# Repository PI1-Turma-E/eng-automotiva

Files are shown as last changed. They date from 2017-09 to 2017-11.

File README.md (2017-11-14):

# Eng-automotiva

# AR2

A AR2 it the robotic arm chosen for use on ultrasound long-distance exam because of it's open source origin.

The arm is converted from the original STEP files to work on CATIA. There is still need to put on bearings and screws on the assembly and to modify or create some stuff to make it work on the final project.

## 6 axis stepper motor robot

This project includes:

- CAD on catia format for working
- Kinematic model

Should be noted that i deleted everything that isn't related to the CAD files.

All geared stepper motors and drivers are available from  [www.omc-stepperonline.com](https://www.omc-stepperonline.com/?tracking=59c1139e8987b) and all other misc. hardware are off-the-shelf items available from multiple sources (see the bill of materials file).

## Information

quick note: **Read the TODO**

really important: **Use the CATIA v5 r19 version** 

Everything here was laid down to us by the guy below, so please pay credit to him.

original git: https://github.com/Chris-Annin/AR2 

Some of the needed parts we will find on [McMaster-carr](https://www.mcmaster.com/)

On the end, we will need to make all the files to print again, as we change the model to fit our needs. If not, we could simply use the original git files to print

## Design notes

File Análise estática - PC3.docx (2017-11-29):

Análise estática

A aplicada ao modelo está presente na figura 1. É possível observar no índice da foto a qualidade dos elementos criados. Em maioria os elementos estão bons para análise estática.

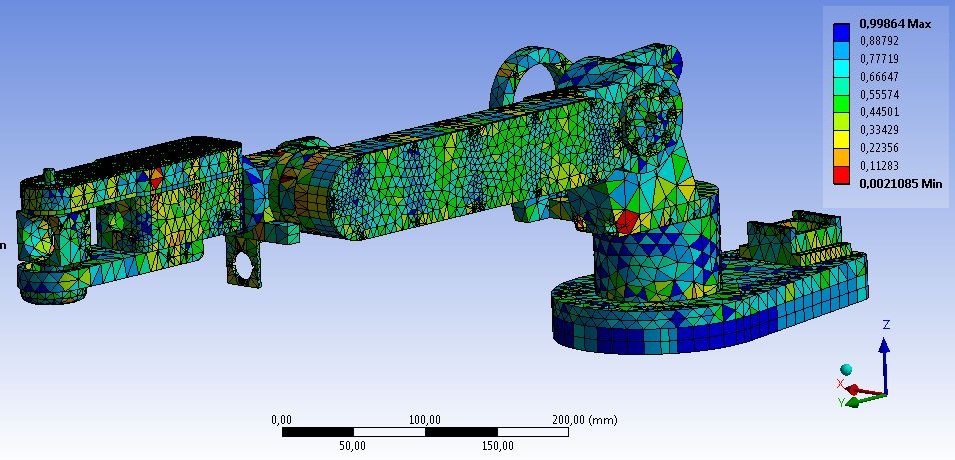
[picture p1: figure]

Figura 1 - Qualidade dos elementos da malha.

Os tipos de elementos utilizados pelo software estão apresentados na figura 2. Os próprios software que gerou os elementos que em maioria são do tipo SOLID187 e SOLID 186.

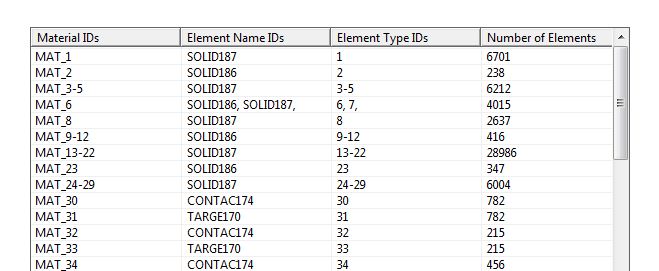
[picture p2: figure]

Figura 2 - Tipos de elementos utilizados na simulação.

As condições de contorno aplicadas foram baseadas no funcionamento estático do braço. O objetivo foi determinar se o material empregado no corpo do braço suportaria o carregamento dos motores e do levantamento do ultrassom. Os locais de aplicação das forças estão representados na figura 3.

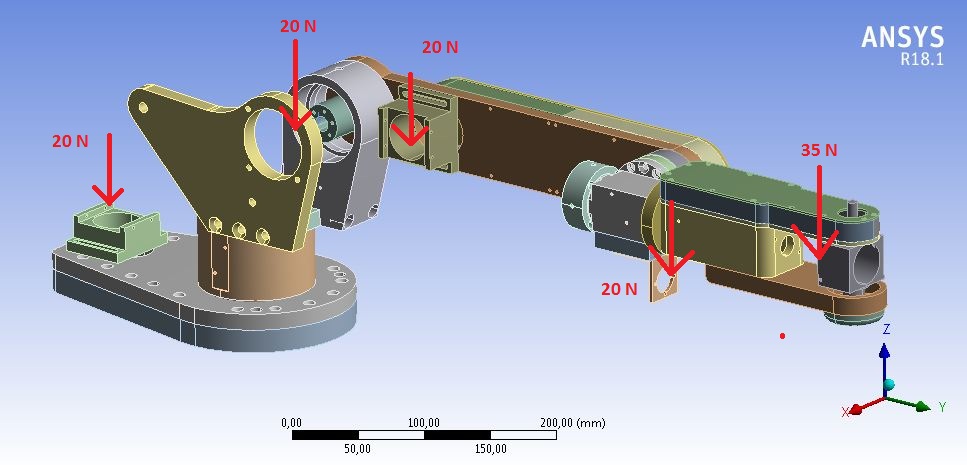
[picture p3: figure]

Figura 3 - Condições de contorno.

Baseado no critério de von Mises, a estrutura teve uma solicitação máxima de aproximadamente 13 mPa. Nessas condições o material empregado suporta as condições estáticas. A figura 4 apresenta esses resultados.

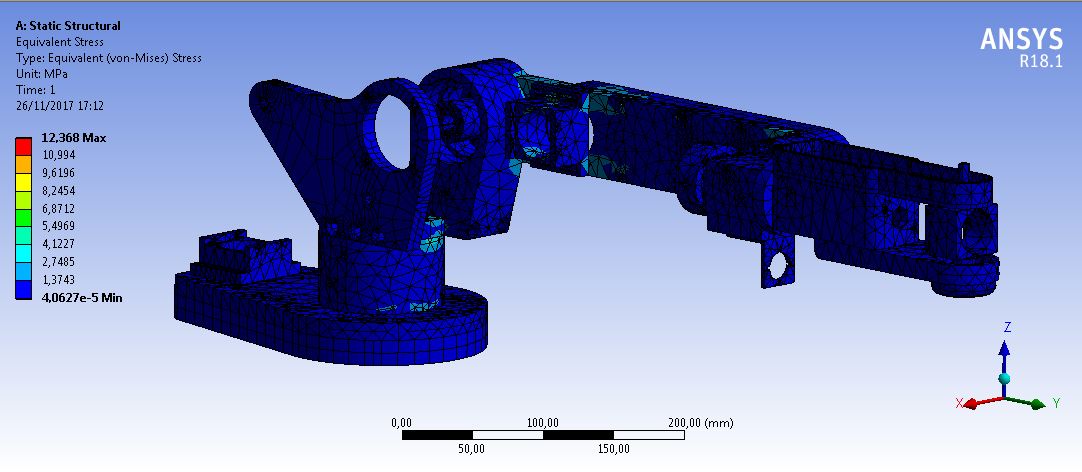
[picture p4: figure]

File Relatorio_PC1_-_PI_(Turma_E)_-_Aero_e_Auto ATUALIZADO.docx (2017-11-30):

Análise e detalhamento de requisitos para o Projeto de Implementação de sistema de telemedicina para exames de ultrassom à distância (Eng. Automotiva/Aeroespacial)

Projeto Integrador 1 – Turma E
Profª: Mariana Costa Bernardes Dias

Gerente de área: Marcos Paulo Miranda Costa

Introdução

Como parte do escopo do Projeto de Implementação de sistema de telemedicina para exames de ultrassom à distância, foi delegada para os alunos das Engenharias Automotiva e Aeroespacial a construção de um braço mecânico capaz de movimentar o transdutor responsável pelo exame de ultrassom. A peça seria uma das partes essenciais do projeto, que tem o objetivo de viabilizar para comunidades carentes e regiões distantes dos grandes centros urbanos a realização de exames de ultrassom e o acesso ao atendimento médico de qualidade.
Para atender às necessidades de projeto, foi definida uma série de pré-requisitos iniciais, dentre os quais estão a capacidade da peça em se movimentar com eficiência (translação e rotação), a leveza dos materiais e a transportabilidade do braço em caso de transferência de equipamentos, bem como a confiabilidade e segurança das peças para a utilização em ambiente hospitalar (médico). Todos os requisitos estabelecidos são devidamente detalhados ao longo deste trabalho. Uma vez que o objetivo do projeto está em realizar exames à distância, também fora decidido que o braço mecânico teria de ser controlado por meio de mecanismos eletrônicos, com base na manipulação de um joystick por um médico especializado em uma unidade de controle pré-definida. O controle do equipamento seria então efetuado via internet, sem que fosse necessária a presença do médico nos locais de exame, estes muitas vezes de difícil acesso.
O projeto foi efetuado numa colaboração entre os alunos das Engenharias Automotiva, Aeroespacial, Eletrônica, Energia e de Software, durante a disciplina de Projeto Integrador 1 da Universidade de Brasília (UnB) – Campus Gama. Cada área tornou-se responsável por uma função no projeto, com o objetivo de entregar ao final da disciplina um protótipo funcional da ideia inicialmente proposta pelo professor.

Objetivo

O objetivo do presente trabalho consiste na construção de um braço mecânico capaz de movimentar o transdutor responsável pela realização de exames de ultrassom. Como exigências para o projeto estão a liberdade de movimentação do equipamento (translação e rotação), a leveza dos materiais constituintes e transportabilidade da peça como um todo, assim como a segurança e a confiabilidade da mesma. O braço mecânico constitui uma das partes essenciais do Projeto de Implementação de sistema de telemedicina para exames de ultrassom à distância.


Metodologia

Para que fosse possível a implementação do projeto, o grupo constituído pelos alunos das Engenharias Automotiva e Aeroespacial foi dividido em dois subgrupos de pesquisa e desenvolvimento. O primeiro teve como objetivo a criação de um protótipo em CAD (Catia e/ou similares) reunindo características essenciais do projeto, a exemplo de suas dimensões, formato, materiais, análise estrutural, encaixe de peças, etc no intuito de trazer uma perspectiva concreta do que seria construído em um aparelho real. Para alcançar tal objetivo, o grupo de trabalho teve ainda que pesquisar e analisar iniciativas semelhantes à proposta estabelecida para o braço mecânico, com a intenção de conhecer melhor os equipamentos já desenvolvidos na área médica para tal fim. O segundo subgrupo criado, por sua vez, teve a função de análise e escolha dos materiais que irão compor o braço mecânico como um todo. Questões como leveza, transportabilidade, viabilidade econômica e usinabilidade dos materiais foram extensamente analisadas por este grupo para enfim determinar do que seria construído o braço mecânico. Ambos os grupos tiveram que fundamentar sua pesquisa em normas e características que fornecessem segurança e confiabilidade, tanto para a execução do projeto quanto para o funcionamento do equipamento.

Projeto do braço mecânico em CAD

Inicialmente, para o projeto do braço mecânico, foi necessário definir quais funções o equipamento teria de executar. Nesse contexto, foram consultados artigos e referências na área médica relativa a exames de ultrassom, para se ter uma noção do que seria necessário implementar no projeto da peça. Após o período de pesquisa, e segundo[1][3][4][5], a construção do braço mecânico teve que levar em consideração fatores como mobilidade, capacidade de carregar um transdutor de 400g e ter movimentação eficiente em translação e rotação, alto grau de precisão, leveza e transportabilidade de materiais, bem como a segurança em um ambiente hospitalar. Para os fins do projeto da disciplina, o equipamento teria ainda que atender a requisitos de viabilidade econômica.
Dentre as iniciativas encontradas no mercado, uma chamou a atenção em específico por conter todas as características exigidas para o projeto. Trata-se de um braço mecânico desenvolvido por Chris Annin [6]. O braço mecânico de Chris Annin foi escolhido graças ao seu alto grau de precisão e segurança durante o contato com o paciente. O grupo de trabalho decidiu tomar o projeto como base para a confecção de um braço semelhante, mas com a capacidade de ser controlado à distância via internet por um joystick manipulado por um médico especializado em uma unidade de controle pré-definida.









O braço mecânico teria o seguinte formato:


Figura 1: Desenho Braço mecânico para uso na área biomédica. Fonte: BATALHA, Wagner Clemente Coelho, Projeto da disciplina Projeto Integrador 1 da Faculdade do Gama, FGA-UNB. Brasília, DF, Brasil, 2017.

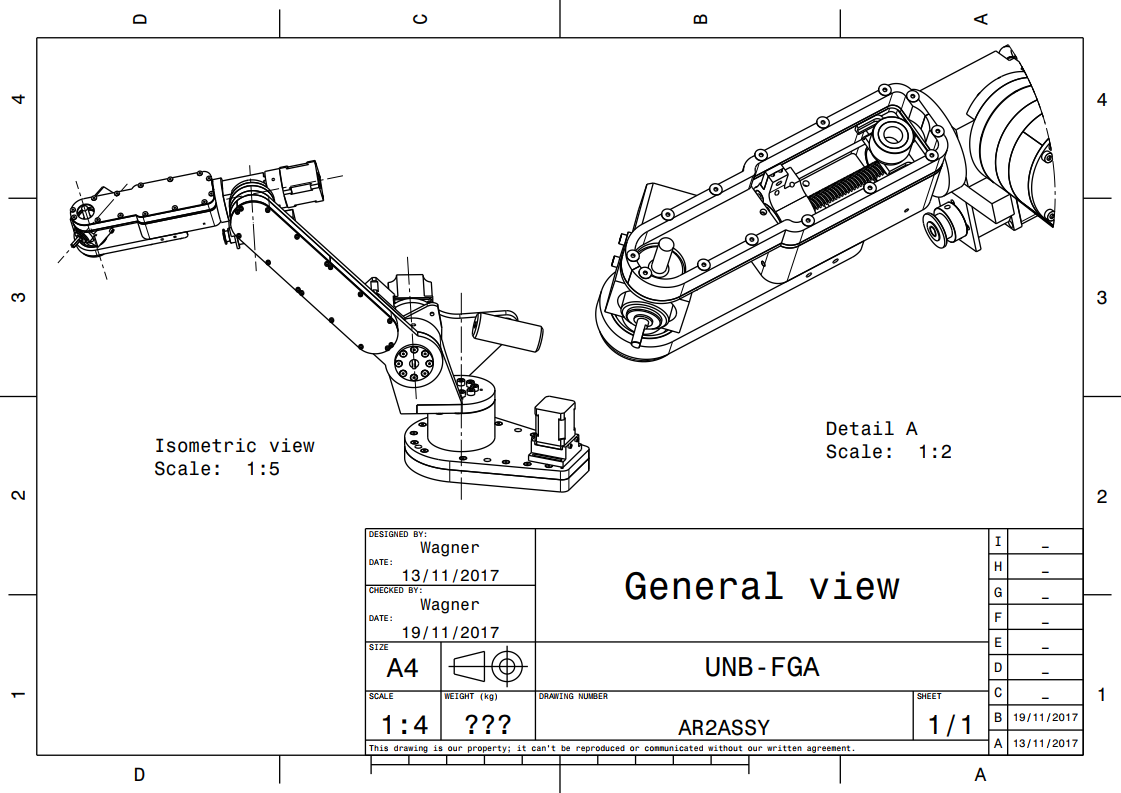
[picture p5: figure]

O formato e a constituição do equipamento como é descrito na Figura 1 se deve aos requisitos citados anteriormente. Este modelo contará com 6 motores de passo em suas articulações e em sua base, o que fornece alto grau de precisão e facilidade em seus controles a distância. Os materiais escolhidos para o projeto foram escolhidos com foco em alcançar o menor peso possível ao final do projeto para maior facilidade de locomoção de suas peças e transporte do braço. Em tópicos posteriores será explicado melhor sobre os materiais. O transdutor de 400g conseguirá ser carregado com firmeza peço braço graças a firmeza dos materiais. No trabalho em questão, este será o modelo de braço mecânico a ser construído, com as dimensões definidas de acordo com as necessidades do projeto na parte de Software e Eletrônica. Em conjunto com o grupo de alunos das Engenharias Eletrônica e de Software, o braço será aprimorado com o controle automático à distância, e a inserção desta tecnologia está por conta da análise e pesquisa prévia destes integrantes de projeto.
A modelagem em CAD do braço mecânico foi efetuado no software Catia V5R19, assim como a descrição das medidas e o desenho técnico das peças constituintes. Para a construção do protótipo, será também necessário o uso de uma impressora 3D que, pela facilidade de acesso e viabilidade econômica de materiais, irá proporcionar ao grupo de trabalho a possibilidade de verificar se o braço construído funcionará de maneira satisfatória.

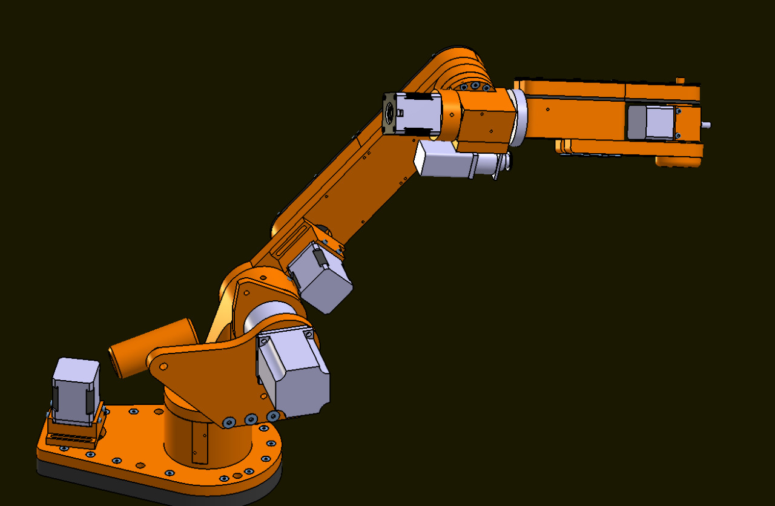
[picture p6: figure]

Figura 2: Desenho 3D do braço mecânico para uso na área biomédica. BATALHA, Wagner Clemente Coelho. Projeto da disciplina Projeto Integrador 1 da Faculdade do Gama, FGA-UNB. Brasília, DF, Brasil,2017.

Pesquisa, análise e escolha de materiais

O projeto apresenta um requisito fundamental para a construção de um braço mecânico, os materiais. Para que se tenha uma otimização melhor do projeto final, é necessário um conhecimento dos materiais a serem utilizados para que eles sejam leves, compactos e perfeitamente transportáveis. O objetivo desta parte do projeto, é definir ou se aproximar ao máximo dos materiais a serem utilizados na construção do braço mecânico. Nesse contexto, após diversos materiais estudados, chegou-se à conclusão de que materiais de impressora 3D poderiam ser utilizados em várias partes do braço mecânico. Por ser um material barato, diminuiria imensamente os custos do projeto se comparado a outros materiais.
Os materiais observados para o projeto são o ABS (acrilonitrilabutadieno estireno) [2], PETG (Politereftalato de etileno glicol) [2] e o alumínio.
O primeiro, ABS, é um material termoplástico derivado do petróleo amplamente utilizado na indústria, um dos principais e mais antigos materiais que vem sido utilizados na impressão 3D. É rígido, bom, ótima resistência a impactos, possui uma leve flexibilidade quando comparada a outros materiais, permitido uma pequena deformação ou flexão da peça,dependendo da sua geometria, o que é bom para peças que necessitem de encaixes em sua montagem. Além de muito resistente a impactos, também é resistente a temperaturas altas.
O segundo, PETG, é um material termoplástico derivado do petróleo, porém reciclável assim como o PET, utilizados na indústria há vários anos para diversas finalidades, mas, recentemente, sendo usando na impressão 3D. Apresenta um aspecto transparente e brilhoso. Produz peças tão resistentes a impactos quanto ao ABS, mas com flexilidade e resistência ligeiramente superior a este. Resiste às altas temperaturas, mas não tanto como o ABS. O que o torna ideal para peças que precisem de transparência ou encaixes com maior flexibilidade, mantendo a alta resistência.

Tabela 1. Comparação entre PETG e ABS

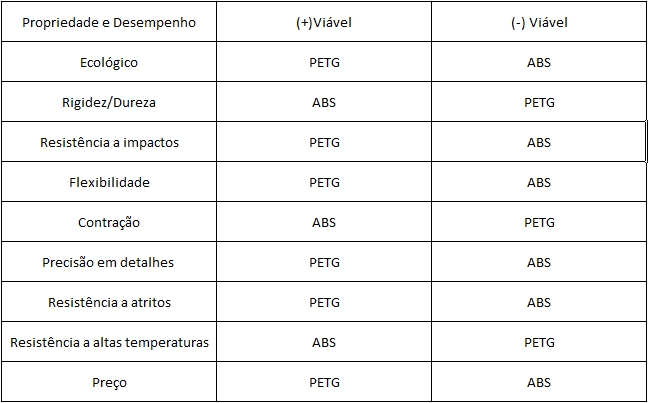
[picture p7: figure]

Analisando a tabela 1 é perceptível que o material termoplástico PETG é mais qualificado devido ao maior número de propriedades mais viáveis. Mas caso os critérios observados favoreçam o material ABS, nada o impede de ser selecionado para o projeto final do braço mecânico.

O terceiro material para analise, o alumínio, é um dos materiais mais utilizados no mundo para fins semelhantes. São inúmeras razões para escolha desse material, podendo ser citadas sua elevada resistência mecânica, sua aparência elegante para hospitais e centro de saúdes, seu valor baixo em comparação a outros metais no mercado, sua leveza e maleabilidade, longa durabilidade, segurança (sendo um material à prova de fogo), durabilidade, alta resistência térmica e baixa necessidade de manutenção. Todas essas razões fazem do alumínio a principal e a mais provável escolha para a construção do braço mecânico.

Para maior organização dos materiais necessários para a construção do braço mecânico AR2, foi montado o Bill of Material (BOM) do projeto, contendo quantidade necessária e a fonte de cada peça.

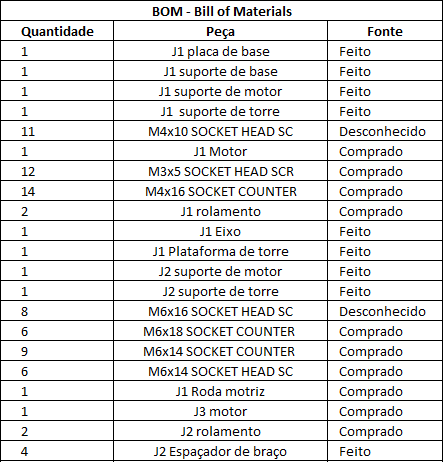
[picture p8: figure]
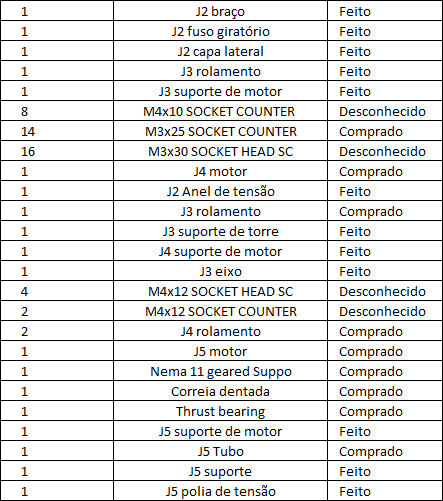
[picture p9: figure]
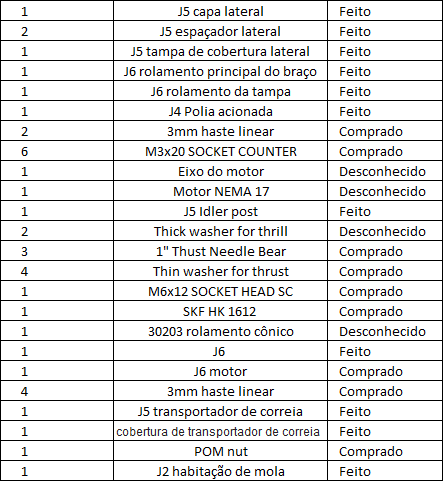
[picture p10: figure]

Figura 3: Bill of Material do braço mecânico. BATALHA, Wagner Clemente Coelho. Projeto da disciplina Projeto Integrador 1 da Faculdade do Gama, FGA-UNB. Brasília, DF, Brasil,2017.

Conclusão

A construção de um braço mecânico para atender ao Projeto de Implementação de sistema de telemedicina para exames de ultrassom à distância foi dividida em dois subgrupos de trabalho. O primeiro teve que se comprometer na realização de um protótipo em CAD reunindo as informações essenciais do projeto. Nesse caso, a aplicação dos conceitos desenvolvidos em Desenho Mecânico Assistido por Computador, bem como o conhecimento em Materiais de Construção para Engenharia foram fundamentais para que fosse possível implementar o protótipo. O segundo subgrupo, por sua vez, ficou por conta da análise, pesquisa e escolha dos materiais que iriam constituir o braço mecânico como um todo. Ambas as divisões de trabalho possibilitaram aos integrantes de projeto a aplicação de seus conceitos teóricos desenvolvidos em sala e a capacidade de desenvolver, na prática, um protótipo inovador e funcional para uma aplicação na área biomédica. O projeto ainda foi de fundamental importância para a compreensão do propósito da Engenharia em melhorar a qualidade de vida de muitas pessoas.

Referências bibliográficas

[1] NUNES, LUIS F. DE OLIVEIRA MELLO,Projeto e fabricação de um braço mecânico para ultrassom médico,Projeto de graduação, UFRJ/ESCOLA POLITÉCNICA, Rio de Janeiro, RJ, Brasil, 2015.

[2] Conheça os diferentes tipos de materiais para impressão 3D FDM. 1 Dez. 2015. IMPRESSAO3DFACIL. Disponível em: <http://www.impressao3dfacil.com.br/conheca-os-diferentes-tipos-de-materiais-para-impressao-3d-fdm/>. Acesso em: 16 Set. 2017.

[3]Richard S. Dargan. TeleroboticUltrasound MayRevolutionizeTelemedicine. http://www.rsna.org/News.aspx?id=17929/, 2015. [Online; acessado em 13 de setembro de 2017].

[4] Kim Mathiassen, J.EngerFjellin, KyrreGlette, Per Kristian Hol, andOle Jakob Elle. Na ultrasoundrobotic system usingthecomercial robot ur5. Frontiers in Roboticsand AI, 3:1, 2016.

[5] FrancoisPierrot, EtienneDombre, Eric Degoulange, L. Urbain, Pierre Caron, SylvieBoudet, J_eromeGariepy, and Jean-Louis Megnien. Hippocrate: A safe robotarmformedicalapplicationswith force feedback. Medical imageanalysis, 3(3):285{300, 1999.

[6] AR2 - 6 axis stepper motor robot and control software Set, 2017. GITHUB. Disponível em: <https://github.com/Chris-Annin/AR2>. Acesso em: 30 Nov. 2017.

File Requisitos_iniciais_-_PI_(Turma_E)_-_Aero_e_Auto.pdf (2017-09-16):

Lista inicial de requisitos para a realização do Projeto de Implementação de sistema de telemedicina para exames de ultrassom à distância (Eng. Automotiva/Aeroespacial)

Projeto Integrador 1 – Turma E
Profª: Mariana Costa Bernardes Dias

Gerente: Marcos Paulo Miranda Costa

Requisitos iniciais verificados:

1º) Projeto de braço mecânico em CAD: Para a realização do projeto, verificou-se como necessária a construção de um braço mecânico para a realização dos exames de ultrassonografia à distância, este que será controlado por um operador habilitado e qualificado para concluir os diagnósticos e enviá-los ao paciente o mais rápido possível. Nesse contexto, uma vez que trata-se de um projeto inovador, a construção do protótipo de um braço mecânico em CAD (Catia ou similar) contendo suas características essenciais é fundamental para a constituição do projeto como um todo. A ideia é reunir no protótipo aspectos como dimensões, formato, análise estrutural, materiais, encaixe de peças, etc no intuito de trazer uma perspectiva concreta do que seria construído em um aparelho real.

Integrantes responsáveis:
Marcos Paulo Costa (Gerente); Lucas Régis;
Igor Lima;
Wagner;

2º) Pesquisa de materiais (braço mecânico): Outro requisito fundamental está na escolha dos materiais que irão compor o braço mecânico solicitado para o projeto. Levando em conta que o propósito do aparelho seria a realização de exames à distância, os materiais que deverão ser selecionados terão que ser leves e perfeitamente transportáveis, além de permitirem que o braço tenha mobilidade para o exame e alcance ao menos o torço inteiro de uma pessoa.

Integrantes responsáveis:
Mathews Leles;
Roberto;
Luis Lahr;
Jônatas Ribeiro;

3º) Análise de segurança: O braço mecânico também deve passar por uma análise de segurança, tanto no que diz respeito ao projeto em CAD quanto na escolha de materiais. Como se trata de um equipamento médico, é necessário ainda checar as normas para o funcionamento adequado do equipamento.
Obs.: Todos os integrantes do grupo terão de efetuar a análise de segurança de suas respectivas partes (projeto em CAD e pesquisa de materiais).

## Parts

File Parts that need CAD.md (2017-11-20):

# This is the List of all CAD needed parts.
## General recomendations

If you dont have the CATIA V5 r19, please send the file as an STEP file format.

Whoever is in charge of a part, should find the correct dimensions of said piece. 
Keep in mind, that you don't need to make a very complex part, make it as simple 
as you can, with the main elements visible. For example, you don't need to make 
the teeth on sprockets or gears and as well you should't make 3d threads because
they aren't very usable, but you need to make the holes for screws because these 
are usable elements.

If you find any part on the web, please cite the link here.

## Parts list
  
- Already Made Parts
  - 30203 Tapered Bearing (Lucas Regis)
  - Thrust Needle Roller Bearing 35x52x4 (Lucas Regis)
  - SKF HK 1612 Needle Roller Bearing Caged 16mmID 22mmOD 12Width (Lucas Regis)
  - LM3UU 3mm Linear Bearing (Igor Lima)
  - 688Z Deep Groove Bearing (Igor Lima)
  - 19:1 Planetary Gear 14HS13-0804S-PG19 NEMA 14 Stepper Motor (Luís filipe)
  - 47:1 Planetary Gear 23HS30-2804S-PG47 NEMA 23 Stepper Motor (Jonatas)
  - 5:1 Planetary Gear 11HS20-0674S-PG5 NEMA 11 Stepper Motor (Jonatas)
  - NEMA 11 Stepper Motor (Geared motor) Support (Jonatas)
  - 5:1 Planetary Gear 17HS19-1684S-PG5 NEMA 17 Stepper Motor (Marcos Paulo)
  - 19:1 Planetary Gear 17HS19-1684S-PG19 NEMA 17 Stepper Motor (Marcos Paulo)
  - Threaded Rod NEMA 17 external link 200mm T8 x 8 (Marcos Paulo)
  - 32009 Tapered Bearing
  - 30206 Tapered Bearing
  - 30204 Tapered Bearing
  - 60T Timing Hub Pulley
  - Thrust Needle Roller Bearing 1" x 9/16" **McMaster Catalog = 5909K36**
  - Thrust Needle Roller Bearing 0.032" thick Washer **McMaster Catalog = 5909K49**
  - Thrust Needle Roller Bearing 0.126" thick Washer **McMaster Catalog = 5909K63**
  - Koyo B-1616 Needle Roller Bearing Cup, Open, 1"ID  1-1/4"OD 1"Width
  - 3mm Stainless Steel Linear Rail
  - XL 15 Teeth 8mm Bore 11 Width timing belt Sprocket (Igor Lima)
  - XL 10 Teeth 6mm Bore 11 Width timing belt Sprocket (Luís Filipe)

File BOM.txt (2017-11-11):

Compute Date: quinta-feira, 9 de novembro de 2017 22:19:19 

===================================================================================== 
= Bill of Material: AR2ASSY                                                         = 
===================================================================================== 
 
+----------+----------------------+------------+---------------------+--------------+ 
| Quantity | Part Number          | Type       | Nomenclature        | Source       | 
+----------+----------------------+------------+---------------------+--------------+ 
| 1        | J6 main bearing arm  | Part       | J6 main bearing arm | Unknown      | 
| 1        | J5 belt carrier clam | Part       | J5 belt carrier cla | Unknown      | 
| 1        | J5 belt carrier      | Part       | J5 belt carrier     | Unknown      | 
| 1        | J5 housing           | Part       | J5 housing          | Unknown      | 
| 1        | J5 idler tension blo | Part       | J5 idler tension bl | Unknown      | 
| 1        | J5 motor mount       | Part       | J5 motor mount      | Unknown      | 
| 1        | J5 side cover cap    | Part       | J5 side cover cap   | Unknown      | 
| 2        | J5 side cover spacer | Part       | J5 side cover space | Unknown      | 
| 1        | J5 side cover        | Part       | J5 side cover       | Unknown      | 
| 1        | J6 bearing cap       | Part       | J6 bearing cap      | Unknown      | 
| 1        | J6 housing single pi | Part       | J6 housing single p | Unknown      | 
| 1        | Joint1               | Assembly   |                     | Unknown      | 
| 2        | 32009 taperedRollerB | Part       | 32009               | Bought       | 
| 1        | J2 Spring housing    | Part       | J2 Spring housing   | Unknown      | 
| 1        | Joint2               | Assembly   |                     | Unknown      | 
| 1        | J2 tension ring      | Part       | J2 tension ring     | Unknown      | 
| 2        | 30206 taperedRollerB | Part       | 30206               | Bought       | 
| 1        | Joint3               | Assembly   |                     | Unknown      | 
| 1        | 30204 taperedRollerB | Part       |                     | Bought       | 
| 1        | J4                   | Assembly   |                     | Unknown      | 
+----------+----------------------+------------+---------------------+--------------+ 

===================================================================================== 
= Bill of Material: Joint1                                                          = 
===================================================================================== 
 
+----------+----------------------+------------+---------------------+--------------+ 
| Quantity | Part Number          | Type       | Nomenclature        | Source       | 
+----------+----------------------+------------+---------------------+--------------+ 
| 1        | J1 base plate        | Part       | J1 base plate       | Unknown      | 
| 1        | J1 base support spac | Part       | J1 base support spa | Unknown      | 
| 1        | J1 motor mount       | Part       | J1 motor mount      | Unknown      | 
| 1        | J1 turret housing    | Part       | J1 turret housing   | Unknown      | 
| 8        | M4x10 SOCKET HEAD SC | Part       |                     | Unknown      | 
+----------+----------------------+------------+---------------------+--------------+ 

===================================================================================== 
= Bill of Material: Joint2                                                          = 
===================================================================================== 
 
+----------+----------------------+------------+---------------------+--------------+ 
| Quantity | Part Number          | Type       | Nomenclature        | Source       | 
+----------+----------------------+------------+---------------------+--------------+ 
| 1        | J1 spindle           | Part       | J1 spindle          | Unknown      | 
| 1        | J1 turret platform   | Part       | J1 turret platform  | Unknown      | 
| 1        | J2 motor support     | Part       | J2 motor support    | Unknown      | 
| 1        | J2 turret housing    | Part       | J2 turret housing   | Unknown      | 
| 8        | M6x16 SOCKET HEAD SC | Part       |                     | Unknown      | 
| 6        | M6x18 SOCKET COUNTER | Part       |                     | Bought       | 
| 3        | M6x14 SOCKET COUNTER | Part       |                     | Bought       | 
| 6        | M6x14 SOCKET HEAD SC | Part       |                     | Bought       | 
| 1        | J1 Driven Sprocket   | Part       |                     | Bought       | 
+----------+----------------------+------------+---------------------+--------------+ 

===================================================================================== 
= Bill of Material: Joint3                                                          = 
===================================================================================== 
 
+----------+----------------------+------------+---------------------+--------------+ 
| Quantity | Part Number          | Type       | Nomenclature        | Source       | 
+----------+----------------------+------------+---------------------+--------------+ 
| 4        | J2 arm cover spacer  | Part       | J2 arm cover spacer | Unknown      | 
| 1        | J2 arm               | Part       | J2 arm              | Unknown      | 
| 1        | J2 drive spindle     | Part       | J2 drive spindle    | Unknown      | 
| 1        | J2 side cover        | Part       | J2 side cover       | Unknown      | 
| 1        | J3 bearing cup       | Part       | J3 bearing cup      | Unknown      | 
| 1        | J3 motor mount       | Part       | J3 motor mount      | Unknown      | 
| 8        | M4x10 SOCKET COUNTER | Part       |                     | Unknown      | 
| 6        | M3x25 SOCKET COUNTER | Part       |                     | Bought       | 
| 16       | M3x30 SOCKET HEAD SC | Part       |                     | Unknown      | 
+----------+----------------------+------------+---------------------+--------------+ 

===================================================================================== 
= Bill of Material: J4                                                              = 
===================================================================================== 
 
+----------+----------------------+------------+---------------------+--------------+ 
| Quantity | Part Number          | Type       | Nomenclature        | Source       | 
+----------+----------------------+------------+---------------------+--------------+ 
| 1        | J3 turret housing    | Part       | J3 turret housing   | Unknown      | 
| 1        | J4 motor mount - lim | Part       | J4 motor mount - li | Unknown      | 
| 1        | J3 spindle           | Part       | J3 spindle          | Unknown      | 
| 4        | M4x12 SOCKET HEAD SC | Part       |                     | Unknown      | 
| 2        | M4x12 SOCKET COUNTER | Part       |                     | Unknown      | 
+----------+----------------------+------------+---------------------+--------------+ 

=================================== 
= Recapitulation of: AR2ASSY      = 
= Different parts: 44             = 
= Total parts: 107                = 
=================================== 
 
+----------+----------------------+ 
| Quantity | Part Number          | 
+----------+----------------------+ 
| 1        | J6 main bearing arm  | 
| 1        | J5 belt carrier clam | 
| 1        | J5 belt carrier      | 
| 1        | J5 housing           | 
| 1        | J5 idler tension blo | 
| 1        | J5 motor mount       | 
| 1        | J5 side cover cap    | 
| 2        | J5 side cover spacer | 
| 1        | J5 side cover        | 
| 1        | J6 bearing cap       | 
| 1        | J6 housing single pi | 
| 1        | J1 base plate        | 
| 1        | J1 base support spac | 
| 1        | J1 motor mount       | 
| 1        | J1 turret housing    | 
| 8        | M4x10 SOCKET HEAD SC | 
| 2        | 32009 taperedRollerB | 
| 1        | J2 Spring housing    | 
| 1        | J1 spindle           | 
| 1        | J1 turret platform   | 
| 1        | J2 motor support     | 
| 1        | J2 turret housing    | 
| 8        | M6x16 SOCKET HEAD SC | 
| 6        | M6x18 SOCKET COUNTER | 
| 3        | M6x14 SOCKET COUNTER | 
| 6        | M6x14 SOCKET HEAD SC | 
| 1        | J1 Driven Sprocket   | 
| 1        | J2 tension ring      | 
| 2        | 30206 taperedRollerB | 
| 4        | J2 arm cover spacer  | 
| 1        | J2 arm               | 
| 1        | J2 drive spindle     | 
| 1        | J2 side cover        | 
| 1        | J3 bearing cup       | 
| 1        | J3 motor mount       | 
| 8        | M4x10 SOCKET COUNTER | 
| 6        | M3x25 SOCKET COUNTER | 
| 16       | M3x30 SOCKET HEAD SC | 
| 1        | 30204 taperedRollerB | 
| 1        | J3 turret housing    | 
| 1        | J4 motor mount - lim | 
| 1        | J3 spindle           | 
| 4        | M4x12 SOCKET HEAD SC | 
| 2        | M4x12 SOCKET COUNTER | 
+----------+----------------------+

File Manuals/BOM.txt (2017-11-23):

Compute Date: quinta-feira, 23 de novembro de 2017 20:07:28 
 
Used Search Order: [None] 
 
============================================================================================== 
= Bill of Material: AR2ASSY                                                                  = 
============================================================================================== 
 
+----------+----------------------+---------------------+--------------+---------------------+ 
| Quantity | Part Number          | Nomenclature        | Source       | Definition          | 
+----------+----------------------+---------------------+--------------+---------------------+ 
| 1        | Joint1               |                     | Unknown      | Base                | 
| 1        | Joint2               |                     | Unknown      |                     | 
| 1        | Joint3               |                     | Unknown      |                     | 
| 1        | Joint4               |                     | Unknown      |                     | 
| 1        | Joint5               |                     | Unknown      |                     | 
| 1        | Joint6               |                     | Unknown      |                     | 
| 1        | Belt Carrier         |                     | Unknown      |                     | 
| 1        | J2 Spring housing    | J2 Spring housing   | Made         |                     | 
+----------+----------------------+---------------------+--------------+---------------------+ 

============================================================================================== 
= Bill of Material: Joint1                                                                   = 
============================================================================================== 
 
+----------+----------------------+---------------------+--------------+---------------------+ 
| Quantity | Part Number          | Nomenclature        | Source       | Definition          | 
+----------+----------------------+---------------------+--------------+---------------------+ 
| 1        | J1 base plate        | J1 base plate       | Made         |                     | 
| 1        | J1 base support spac | J1 base support spa | Made         |                     | 
| 1        | J1 motor mount       | J1 motor mount      | Made         | UNKNOWN             | 
| 1        | J1 turret housing    | J1 turret housing   | Made         |                     | 
| 8        | M4x10 SOCKET HEAD SC |                     | Unknown      |                     | 
| 1        | J1 Motor             | Planetary Gear 17HS | Bought       | stepper motor       | 
| 4        | M3x5 SOCKET HEAD SCR |                     | Bought       |                     | 
| 14       | M4x16 SOCKET COUNTER |                     | Bought       |                     | 
| 2        | J1 Bearing           | 32009 Taperd Roller | Bought       |                     | 
+----------+----------------------+---------------------+--------------+---------------------+ 

============================================================================================== 
= Bill of Material: Joint2                                                                   = 
============================================================================================== 
 
+----------+----------------------+---------------------+--------------+---------------------+ 
| Quantity | Part Number          | Nomenclature        | Source       | Definition          | 
+----------+----------------------+---------------------+--------------+---------------------+ 
| 1        | J1 spindle           | J1 spindle          | Made         |                     | 
| 1        | J1 turret platform   | J1 turret platform  | Made         |                     | 
| 1        | J2 motor support     | J2 motor support    | Made         |                     | 
| 1        | J2 turret housing    | J2 turret housing   | Made         |                     | 
| 8        | M6x16 SOCKET HEAD SC |                     | Unknown      |                     | 
| 6        | M6x18 SOCKET COUNTER |                     | Bought       |                     | 
| 3        | M6x14 SOCKET COUNTER |                     | Bought       |                     | 
| 6        | M6x14 SOCKET HEAD SC |                     | Bought       |                     | 
| 1        | J1 Driven Sprocket   |                     | Bought       | 60T timing Pulley   | 
| 1        | J3Motor              |                     | Bought       | 23HS30-2804S-PG47 N | 
| 2        | J2 Bearing           | 30206 taperedRoller | Bought       |                     | 
+----------+----------------------+---------------------+--------------+---------------------+ 

============================================================================================== 
= Bill of Material: Joint3                                                                   = 
============================================================================================== 
 
+----------+----------------------+---------------------+--------------+---------------------+ 
| Quantity | Part Number          | Nomenclature        | Source       | Definition          | 
+----------+----------------------+---------------------+--------------+---------------------+ 
| 4        | J2 arm cover spacer  | J2 arm cover spacer | Made         |                     | 
| 1        | J2 arm               | J2 arm              | Made         |                     | 
| 1        | J2 drive spindle     | J2 drive spindle    | Made         |                     | 
| 1        | J2 side cover        | J2 side cover       | Made         |                     | 
| 1        | J3 bearing cup       | J3 bearing cup      | Made         |                     | 
| 1        | J3 motor mount       | J3 motor mount      | Made         |                     | 
| 8        | M4x10 SOCKET COUNTER |                     | Unknown      |                     | 
| 6        | M3x25 SOCKET COUNTER |                     | Bought       |                     | 
| 16       | M3x30 SOCKET HEAD SC |                     | Unknown      |                     | 
| 1        | J4 Motor             | 17HS19-1684S-PG19   | Bought       | Nema 17 Stepper mot | 
| 4        | M3x5 SOCKET HEAD SCR |                     | Bought       |                     | 
| 1        | J2 tension ring      | J2 tension ring     | Made         |                     | 
| 1        | J3 Bearing           |                     | Bought       | 30204 taperedRoller | 
+----------+----------------------+---------------------+--------------+---------------------+ 

============================================================================================== 
= Bill of Material: Joint4                                                                   = 
============================================================================================== 
 
+----------+----------------------+---------------------+--------------+---------------------+ 
| Quantity | Part Number          | Nomenclature        | Source       | Definition          | 
+----------+----------------------+---------------------+--------------+---------------------+ 
| 1        | J3 turret housing    | J3 turret housing   | Made         |                     | 
| 1        | J4 motor mount - lim | J4 motor mount - li | Made         |                     | 
| 1        | J3 spindle           | J3 spindle          | Made         |                     | 
| 4        | M4x12 SOCKET HEAD SC |                     | Unknown      |                     | 
| 2        | M4x12 SOCKET COUNTER |                     | Unknown      |                     | 
| 3        | M4x10 SOCKET HEAD SC |                     | Unknown      |                     | 
| 2        | J4 bearing           | Koyo B-1616 Needle  | Bought       | 1" ID, 1-1/4" OD, 1 | 
| 1        | J5Motor              | 11HS20-0674S-PG5 NE | Bought       |                     | 
| 1        | Nema 11 geared suppo |                     | Bought       |                     | 
| 1        | Timing belt Sprocket |                     | Bought       | XL 10Teeth 6mm Bore | 
| 1        | Thrust needle Bearin | Thrust needle Beari | Bought       |                     | 
+----------+----------------------+---------------------+--------------+---------------------+ 

============================================================================================== 
= Bill of Material: Joint5                                                                   = 
============================================================================================== 
 
+----------+----------------------+---------------------+--------------+---------------------+ 
| Quantity | Part Number          | Nomenclature        | Source       | Definition          | 
+----------+----------------------+---------------------+--------------+---------------------+ 
| 1        | J5 motor mount       | J5 motor mount      | Made         |                     | 
| 1        | J5 Tube              | High-Strength 2024  | Bought       | McMaster 1968T17    | 
| 1        | J5 housing           | J5 housing          | Made         |                     | 
| 1        | J5 idler tension blo | J5 idler tension bl | Made         | UNKNOWN             | 
| 1        | J5 side cover        | J5 side cover       | Made         |                     | 
| 2        | J5 side cover spacer | J5 side cover space | Made         |                     | 
| 1        | J5 side cover cap    | J5 side cover cap   | Made         |                     | 
| 1        | J6 main bearing arm  | J6 main bearing arm | Made         |                     | 
| 1        | J6 bearing cap       | J6 bearing cap      | Made         |                     | 
| 1        | J4 driven Pulley     | 30T for XL 10 Belt  | Made         | 3d Printed          | 
| 6        | M6x14 SOCKET COUNTER |                     | Bought       |                     | 
| 2        | 3mm liner rod        | 3mm Linear rail     | Bought       |                     | 
| 8        | M3x25 SOCKET COUNTER |                     | Bought       |                     | 
| 6        | M3x20 SOCKET COUNTER |                     | Bought       |                     | 
| 1        | Threaded Rod NEMA 17 |                     | Unknown      |                     | 
| 1        | J5 Idler Post        |                     | Made         | 3d Printed          | 
| 2        | Thick Washer For Thr | 0.032" Thick Washer | Unknown      | McMaster 5909K63    | 
| 3        | 1" Thust Needle Bear | 1" Shaft Diameter T | Bought       | McMaster 5909K36    | 
| 4        | Thin Washer For Thru | 0.126" Thick Washer | Bought       | McMaster 5909K49    | 
| 1        | M6x12 SOCKET HEAD SC |                     | Bought       |                     | 
| 1        | SKF HK 1612 Needle R | SKF HK 1612         | Bought       |                     | 
| 1        | 30203 Tapered Bearin |                     | Unknown      |                     | 
+----------+----------------------+---------------------+--------------+---------------------+ 

============================================================================================== 
= Bill of Material: Threaded Rod NEMA 17 external link 200mm T8 x 8                          = 
============================================================================================== 
 
+----------+----------------------+---------------------+--------------+---------------------+ 
| Quantity | Part Number          | Nomenclature        | Source       | Definition          | 
+----------+----------------------+---------------------+--------------+---------------------+ 
| 1        | Eixo_do_motor        |                     | Unknown      |                     | 
| 1        | Motor_NEMA_17        |                     | Unknown      |                     | 
+----------+----------------------+---------------------+--------------+---------------------+ 

============================================================================================== 
= Bill of Material: Joint6                                                                   = 
============================================================================================== 
 
+----------+----------------------+---------------------+--------------+---------------------+ 
| Quantity | Part Number          | Nomenclature        | Source       | Definition          | 
+----------+----------------------+---------------------+--------------+---------------------+ 
| 1        | J6 housing single pi | J6 housing single p | Made         |                     | 
| 1        | J6 Motor             | 14HS13-0804S-PG19 N | Bought       | 5:1 reduction stepp | 
| 4        | M3x5 SOCKET HEAD SCR |                     | Bought       |                     | 
+----------+----------------------+---------------------+--------------+---------------------+ 

============================================================================================== 
= Bill of Material: Belt Carrier                                                             = 
============================================================================================== 
 
+----------+----------------------+---------------------+--------------+---------------------+ 
| Quantity | Part Number          | Nomenclature        | Source       | Definition          | 
+----------+----------------------+---------------------+--------------+---------------------+ 
| 4        | 3mm Linear Bearing   | LM3UU               | Bought       |                     | 
| 1        | J5 belt carrier      | J5 belt carrier     | Made         | UNKNOWN             | 
| 1        | J5 belt carrier clam | J5 belt carrier cla | Made         | UNKNOWN             | 
| 1        | POM nut              |                     | Bought       | T8x8                | 
+----------+----------------------+---------------------+--------------+---------------------+ 

================================================== 
= Recapitulation of: AR2ASSY                     = 
= Different parts: 70                            = 
= Total parts: 190                               = 
================================================== 
 
+----------+----------------------+--------------+ 
| Quantity | Part Number          | Source       | 
+----------+----------------------+--------------+ 
| 1        | J1 base plate        | Made         | 
| 1        | J1 base support spac | Made         | 
| 1        | J1 motor mount       | Made         | 
| 1        | J1 turret housing    | Made         | 
| 11       | M4x10 SOCKET HEAD SC | Unknown      | 
| 1        | J1 Motor             | Bought       | 
| 12       | M3x5 SOCKET HEAD SCR | Bought       | 
| 14       | M4x16 SOCKET COUNTER | Bought       | 
| 2        | J1 Bearing           | Bought       | 
| 1        | J1 spindle           | Made         | 
| 1        | J1 turret platform   | Made         | 
| 1        | J2 motor support     | Made         | 
| 1        | J2 turret housing    | Made         | 
| 8        | M6x16 SOCKET HEAD SC | Unknown      | 
| 6        | M6x18 SOCKET COUNTER | Bought       | 
| 9        | M6x14 SOCKET COUNTER | Bought       | 
| 6        | M6x14 SOCKET HEAD SC | Bought       | 
| 1        | J1 Driven Sprocket   | Bought       | 
| 1        | J3Motor              | Bought       | 
| 2        | J2 Bearing           | Bought       | 
| 4        | J2 arm cover spacer  | Made         | 
| 1        | J2 arm               | Made         | 
| 1        | J2 drive spindle     | Made         | 
| 1        | J2 side cover        | Made         | 
| 1        | J3 bearing cup       | Made         | 
| 1        | J3 motor mount       | Made         | 
| 8        | M4x10 SOCKET COUNTER | Unknown      | 
| 14       | M3x25 SOCKET COUNTER | Bought       | 
| 16       | M3x30 SOCKET HEAD SC | Unknown      | 
| 1        | J4 Motor             | Bought       | 
| 1        | J2 tension ring      | Made         | 
| 1        | J3 Bearing           | Bought       | 
| 1        | J3 turret housing    | Made         | 
| 1        | J4 motor mount - lim | Made         | 
| 1        | J3 spindle           | Made         | 
| 4        | M4x12 SOCKET HEAD SC | Unknown      | 
| 2        | M4x12 SOCKET COUNTER | Unknown      | 
| 2        | J4 bearing           | Bought       | 
| 1        | J5Motor              | Bought       | 
| 1        | Nema 11 geared suppo | Bought       | 
| 1        | Timing belt Sprocket | Bought       | 
| 1        | Thrust needle Bearin | Bought       | 
| 1        | J5 motor mount       | Made         | 
| 1        | J5 Tube              | Bought       | 
| 1        | J5 housing           | Made         | 
| 1        | J5 idler tension blo | Made         | 
| 1        | J5 side cover        | Made         | 
| 2        | J5 side cover spacer | Made         | 
| 1        | J5 side cover cap    | Made         | 
| 1        | J6 main bearing arm  | Made         | 
| 1        | J6 bearing cap       | Made         | 
| 1        | J4 driven Pulley     | Made         | 
| 2        | 3mm liner rod        | Bought       | 
| 6        | M3x20 SOCKET COUNTER | Bought       | 
| 1        | Eixo_do_motor        | Unknown      | 
| 1        | Motor_NEMA_17        | Unknown      | 
| 1        | J5 Idler Post        | Made         | 
| 2        | Thick Washer For Thr | Unknown      | 
| 3        | 1" Thust Needle Bear | Bought       | 
| 4        | Thin Washer For Thru | Bought       | 
| 1        | M6x12 SOCKET HEAD SC | Bought       | 
| 1        | SKF HK 1612 Needle R | Bought       | 
| 1        | 30203 Tapered Bearin | Unknown      | 
| 1        | J6 housing single pi | Made         | 
| 1        | J6 Motor             | Bought       | 
| 4        | 3mm Linear Bearing   | Bought       | 
| 1        | J5 belt carrier      | Made         | 
| 1        | J5 belt carrier clam | Made         | 
| 1        | POM nut              | Bought       | 
| 1        | J2 Spring housing    | Made         | 
+----------+----------------------+--------------+

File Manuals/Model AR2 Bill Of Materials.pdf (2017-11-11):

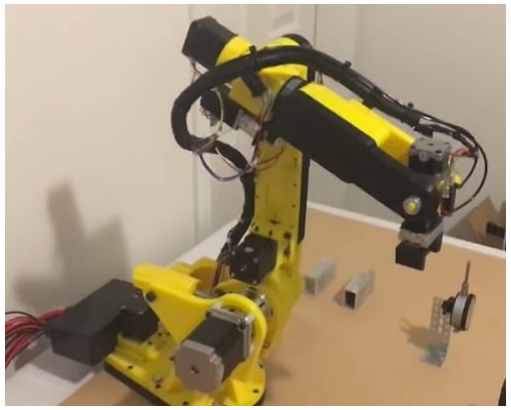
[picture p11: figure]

# Model AR2 Robot

## BILL OF MATERIALS

1 | Bill of Materials

# Printed Components

2

## - Components printed out of ABS

## - Printed with thick shells

## - Printed 2mm thick layers

## - Unless otherwise noted most parts printed 50% solid

### - (spindles and stress bearing components printed 100% solid)

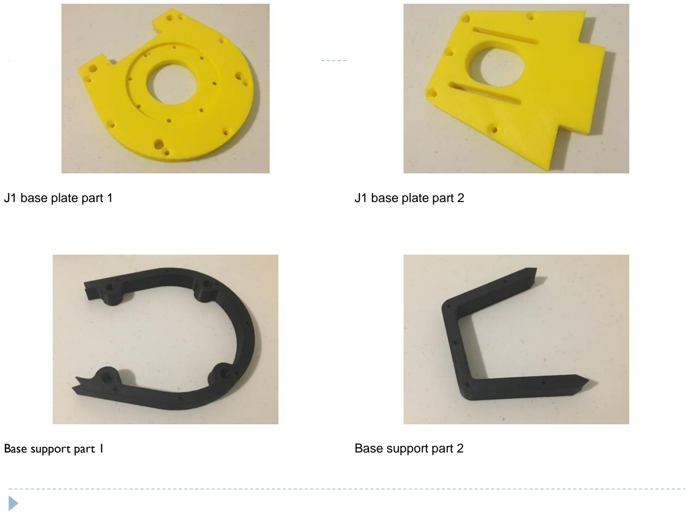
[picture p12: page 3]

J1 base plate part 1 | J1 base plate part 2
Base support part 1 | Base support part 2

J1 alignment plug | J1 spindle
J1 turret housing | J2 turret housing

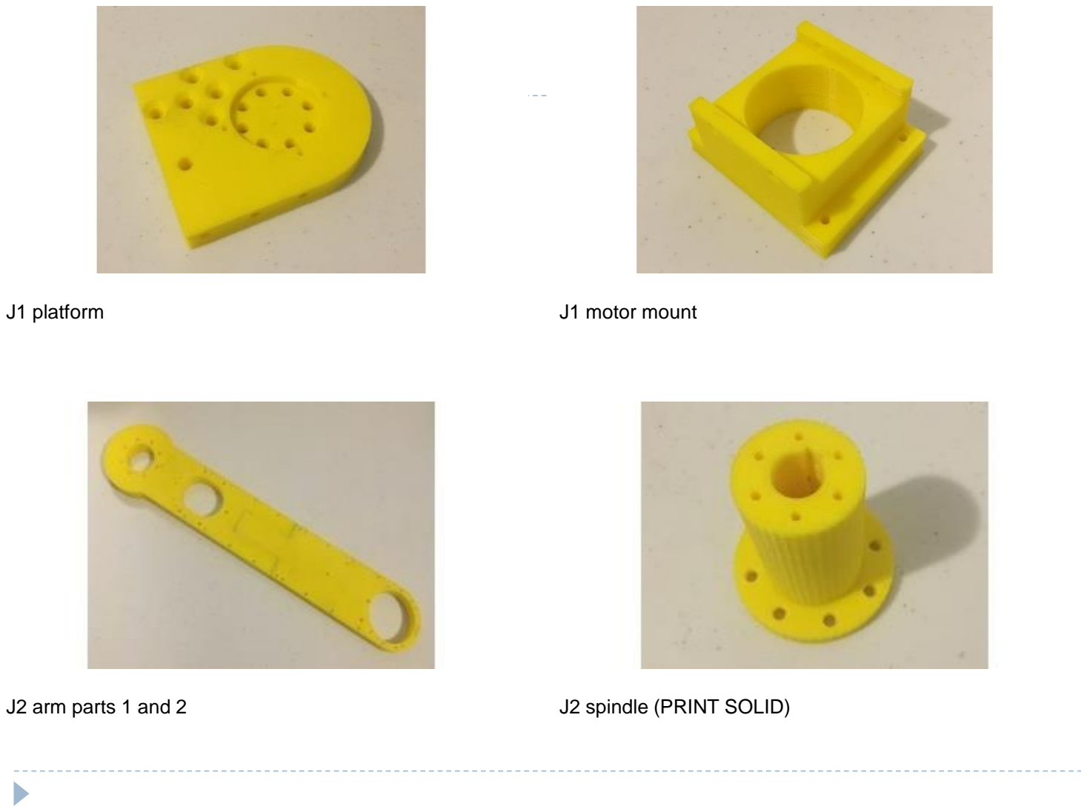
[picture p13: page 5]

J1 platform | J1 motor mount
J2 arm parts 1 and 2 | J2 spindle (PRINT SOLID)

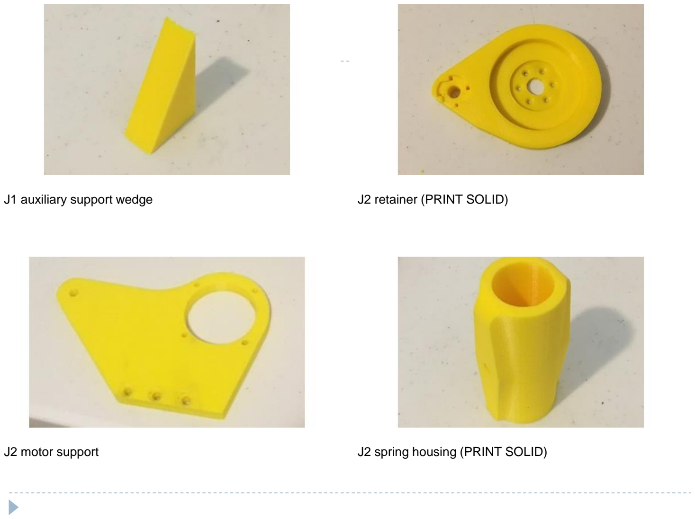
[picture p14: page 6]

J1 auxiliary support wedge | J2 retainer (PRINT SOLID)
J2 motor support | J2 spring housing (PRINT SOLID)

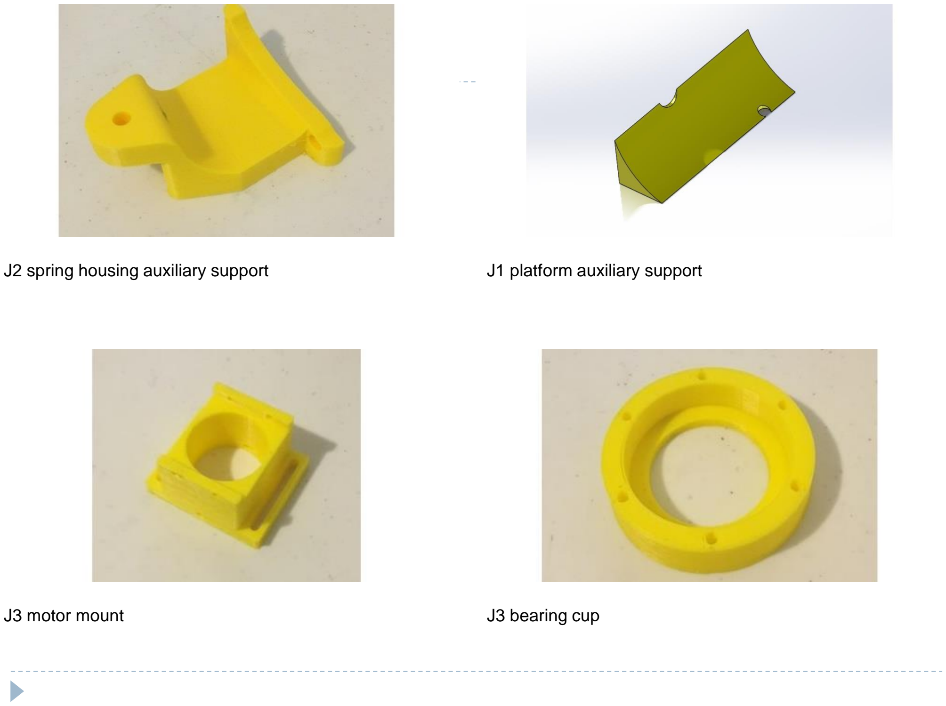
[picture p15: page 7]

J2 spring housing auxiliary support | J1 platform auxiliary support
J3 motor mount | J3 bearing cup

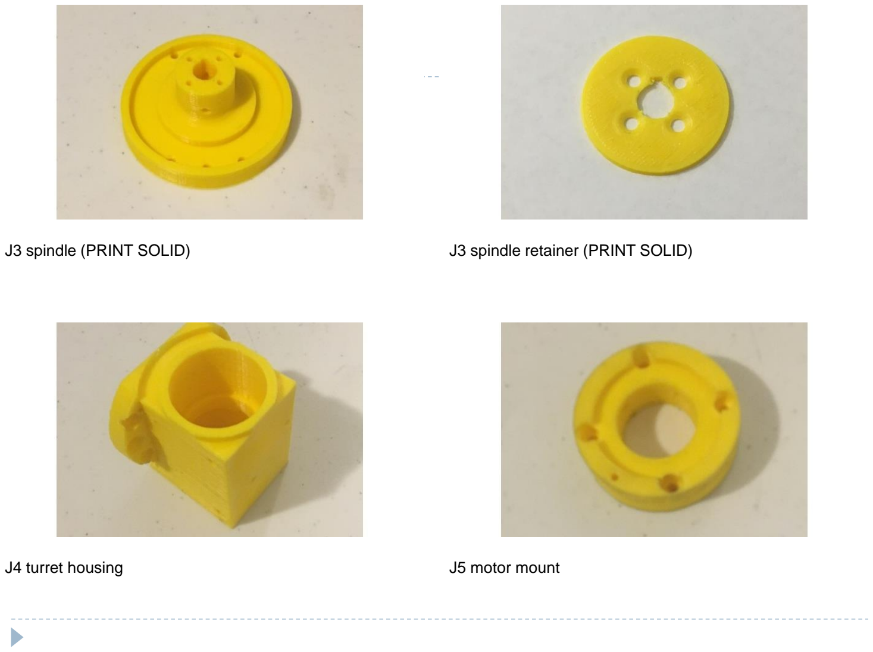
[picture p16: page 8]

J3 spindle (PRINT SOLID) | J3 spindle retainer (PRINT SOLID)
J4 turret housing | J5 motor mount

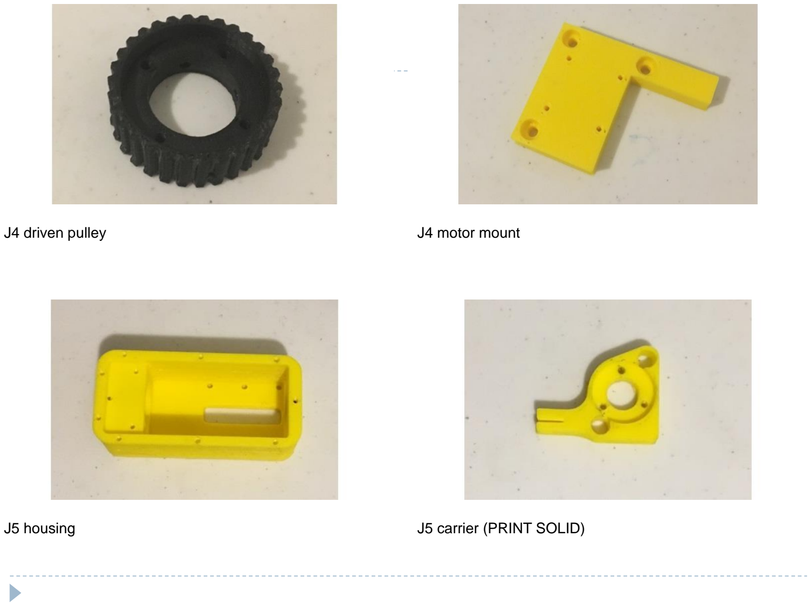
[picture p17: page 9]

J4 driven pulley | J4 motor mount
J5 housing | J5 carrier (PRINT SOLID)

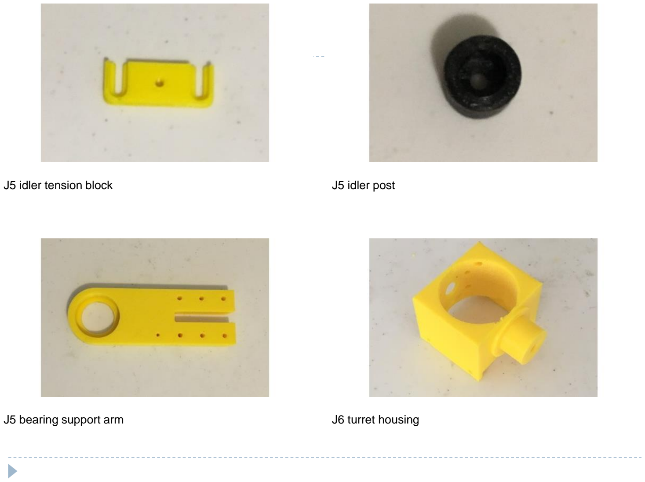
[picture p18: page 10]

J5 idler tension block | J5 idler post
J5 bearing support arm | J6 turret housing


J6 spindle | J6 bearing cap
J5 side cover base | J5 side spacers


J5 side cover cap | J6 gripper mount
J3 side cover spacers | J3 side cover caps

J2 arm auxilliary support

# Stepper Motors

14

### - Geared and linear stepper motors as well as stepper drivers are available from Stepper Online http://www.omc-stepperonline.com/


J1 motor | J2 motor
J3 motor | J4 motor


17LS19-1684E-200G

J4 motor mount bracket | Qty(6) stepper motor drivers

# Bearings

17

Qty. (2) for J1 bearings - Amazon | Qty. (2) for J2 bearings - Amazon
Qty. (1) for J3 bearing - Amazon | Qty. (1) 35mm thrust bearing and washer set for J3 - Amazon


Qty.(3) 1” thrust bearings (2 for J4 and 1 for J6) – McMaster Carr

Qty.(4) (3 for J4 and 1 for J6) –McMaster Carr

Qty.(2) (1 for J4 and 1 for J6) –McMaster Carr | Qty.(2) for J4 bearings - Amazon


Qty. (1) for J5 belt idler - Amazon | Qty.(1) set of 10 shafts (you only need 2) - Amazon
Qty.(1) set of 8 bearings (you only need 2) - Amazon | Qty.(1) set of 10 bearings (you only need 1) - Amazon

Qty.(1) for J6 bearing - Amazon

# Belts - Sprockets

22


Qty. (1) J1 belt - Amazon | Qty (1) J3 belt – or use chain option instead (see instructions) - Amazon

2’ length – J3 chain option (see instructions) – McMaster Carr

Qty.(1) link for J3 – McMaster Carr

Qty.(1) J4 belt – Amazon | Qty.(1) J5 belt – Amazon
Qty.(1) driven pulley for J1 – Amazon | Qty.(4) 15 tooth 8mm bore sprocket (1 for J1 – 2 for J3 if using belt option and 1 for J6) - Ebay


Qty.(2) for J3 chain option – McMaster Carr | Qty.(1) for J4 - Ebay

# Hardware

26


Qty.(1) – McMaster Carr | Qty.(1) – McMaster Carr
Qty.(1) – McMaster Carr | Qty.(1) – McMaster Carr


Qty.(1) McMaster Carr | Qty.(1) McMaster Carr

Qty. (4) spacers purchased at hardware store these are 3/8” x 3/16” x 1” cut down to 15mm long

Qty.(1) McMaster Carr

Qty.(1) set of 10 (you only need 4) - Amazon | Qty.(2) – McMaster Carr
Qty.(1) – McMaster Carr | Qty.(1) – McMaster Carr


Qty.(1) M8 – T nut – Hardware store is more cost effective for a single piece than buying multiple from McMaster Carr

31

QTY | ITEM
7 | M3 x 10 flat head screws
4 | M3 x 10 set screws
12 | M3 x 14 socket head cap screws
14 | M3 x 14 socket head cap screws
44 | M3 x 25 flat head screws
5 | M3 x 3 set screws
28 | M3 x 35 flat head screws
9 | M3 x 6 set screws
1 | M3 x 6 socket head cap screw
6 | M3 x 8 socket head cap screws
8 | M4 nuts
16 | M4 washers
4 | M4 x 10 button head screws
4 | M4 x 10 cap screws
16 | M4 x 10 flat heads
24 | M4 x 10 set screws
23 | M4 x 10 socket head cap screws
2 | M4 x 14 flat head screws
12 | M4 x 20 socket head cap screws
4 | M4 x 35 socket head cap screws
2 | M4 x 6 set screws
31 | M6 x 14 socket head cap screws
15 | M6 x 18 flat head screws

# SCREWS:

(hardware store or
order from McMaster
Carr)

# Electrical Components

32

Qty.(1) – Amazon | Qty.(1) – Amazon
Qty.(1) – Amazon | Qty.(3) – Amazon


Qty.(1) – Stepper Online | Qty.(1) – Amazon
Qty.(1) – Amazon | Qty.(1) – Amazon


Qty.(1) – Amazon | Qty.(1) – Amazon

Qty.(1) – Amazon


Qty.(1) – Amazon | Qty.(1) – Amazon

Qty.(1) – Amazon | Qty.(1) – Amazon
Qty.(2) – Amazon | Qty.(1) – Amazon


Qty.(1) – Amazon | Qty.(2) – Amazon
Qty.(1) – Amazon | Qty.(1) – Amazon


Qty.(1) – Amazon (The ASI terminal blocks list this as the correct jumpers but I had screw type on hand shown in manual)

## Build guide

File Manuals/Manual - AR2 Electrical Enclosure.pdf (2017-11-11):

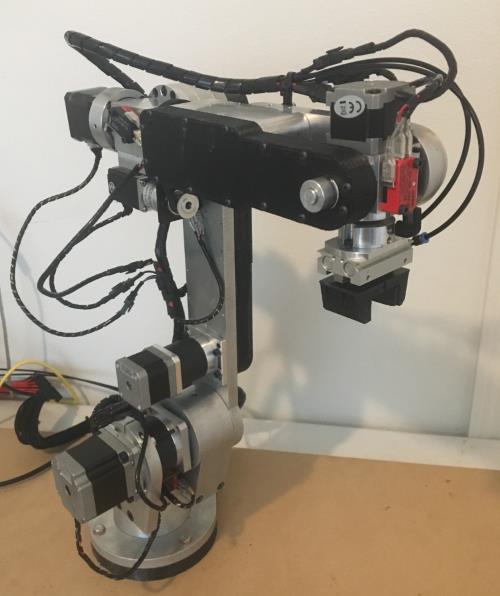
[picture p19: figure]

# Model AR2 Electrical Enclosure

# ELECTRICAL PANEL ASSEMBLY

# NOTES

2

# - THE FIRST REVISION OF THIS CONTROLLER USED ANALOG ST6600 DRIVERS – THE MAJORITY OF THE PICTURES IN THIS MANUAL SHOW THE ST6600 DRIVERS

- *

# - PLEASE NOTE PAGES 11 & 35 SHOW - THE NEW DIGITAL DRIVERS THAT ARE NOW RECOMMENDED FOR THIS BUILD

- *

# - ASIDE FROM THE MODEL OF DRIVERS THE CONSTRUCTION IS NEARLY

IDENTICAL.

# BILL OF MATERIALS

## www.omc-stepperonline.com (https://www.omc-stepperonline.com/?tracking=59c1139e8987b)

3

## All Stepper motors, drivers and power supplies are available at:

## BILL OF MATERIALS CONTINUED

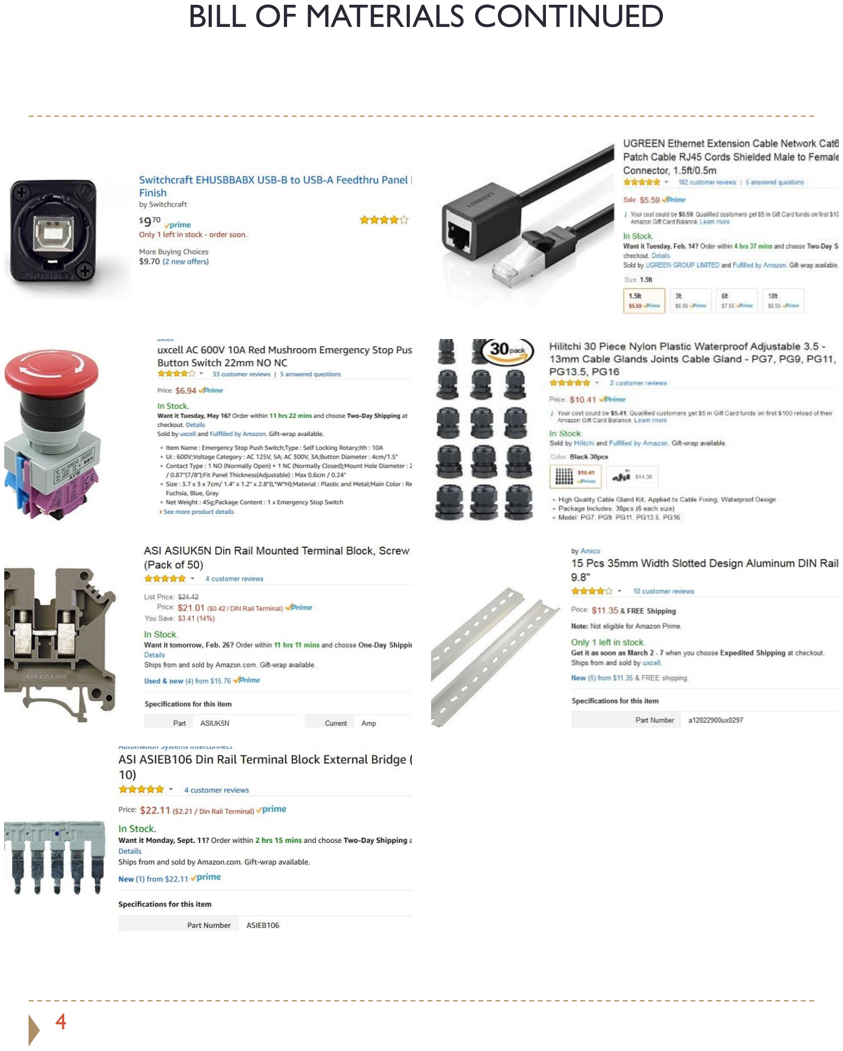
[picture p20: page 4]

4

## BILL OF MATERIALS CONTINUED

5

### Original design used 24vdc power supply with ST-6600 drivers

## Updated design uses DM542T digital drivers for axis 1,2,3,5,6

DM320T for axis 4.

## (this combination is recommended)

## DM542T FOR AXIS

1,2,3,5,6

6

## BILL OF MATERIALS CONTINUED

## DM320T FOR AXIS

4

## ASSEMBLY

Cut 48mm x 30mm rectangular hole in right side of enclosure centered in panel with the top parallel to hasp as shown.

Install backplane into bottom of enclosure using the supplied screws.

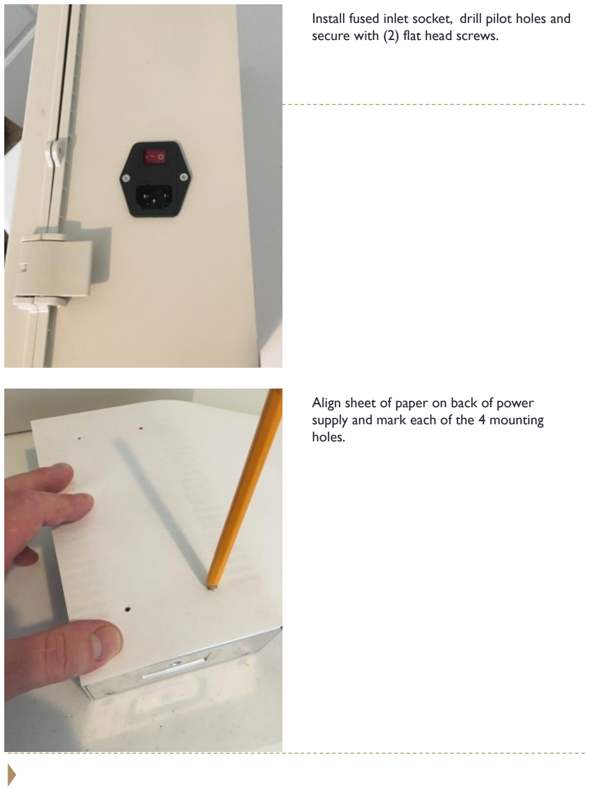
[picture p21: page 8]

Align sheet of paper on back of power supply and mark each of the 4 mounting holes.

Install fused inlet socket, drill pilot holes and secure with (2) flat head screws.

Drill marked holes with 4mm drill bit then secure power supply with (4) 4mm x 10 button head screws to bottom of enclosure.

Align sheet of paper even with backplane and then use marker to transfer the hole pattern.

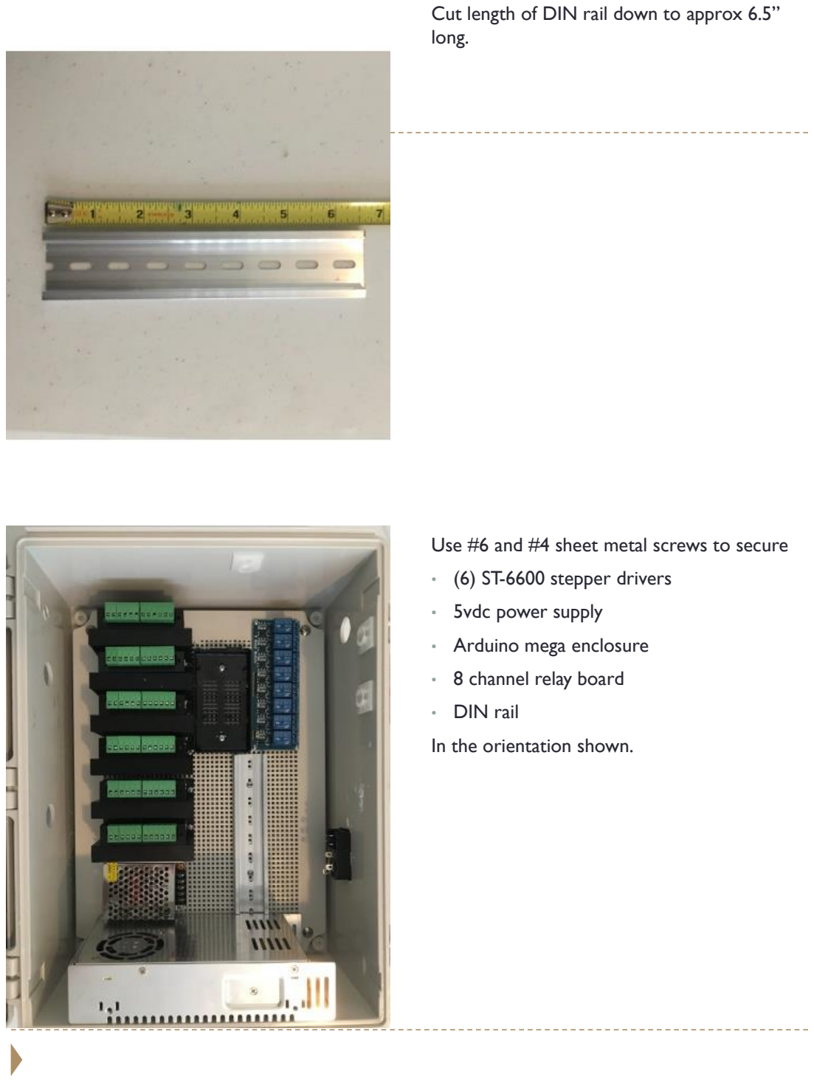
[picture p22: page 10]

Use #6 and #4 sheet metal screws to secure

- (6) ST-6600 stepper drivers
- 5vdc power supply
- Arduino mega enclosure
- 8 channel relay board
- DIN rail

In the orientation shown.

Cut length of DIN rail down to approx 6.5” long.

### -UPDATE-

### This alternate layout places the relay board on the right side providing easier access to the relay terminals. This layout uses (5) DM542T digital stepper drivers and (1) DM320T driver for axis4 instead of the lower cost ST6600 drivers shown

in the majority of this manual.

### NOTE: the smaller DM320T is not shown in this picture as it was incorporated after this picture was taken (see page 35) The smaller DM320T will be the 4th

one down.

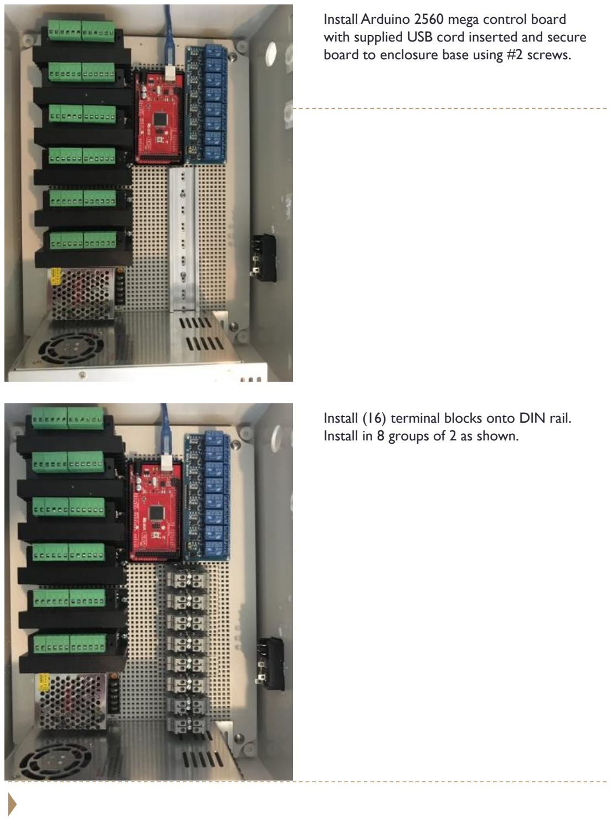
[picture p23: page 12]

Install (16) terminal blocks onto DIN rail. Install in 8 groups of 2 as shown.

Install Arduino 2560 mega control board with supplied USB cord inserted and secure board to enclosure base using #2 screws.

Install green16awg wire from bottom set of terminal blocks to terminal shown on fused inlet socket.

Install terminal jumpers across each set of 2 terminals so that each group of 2 becomes bridged together.

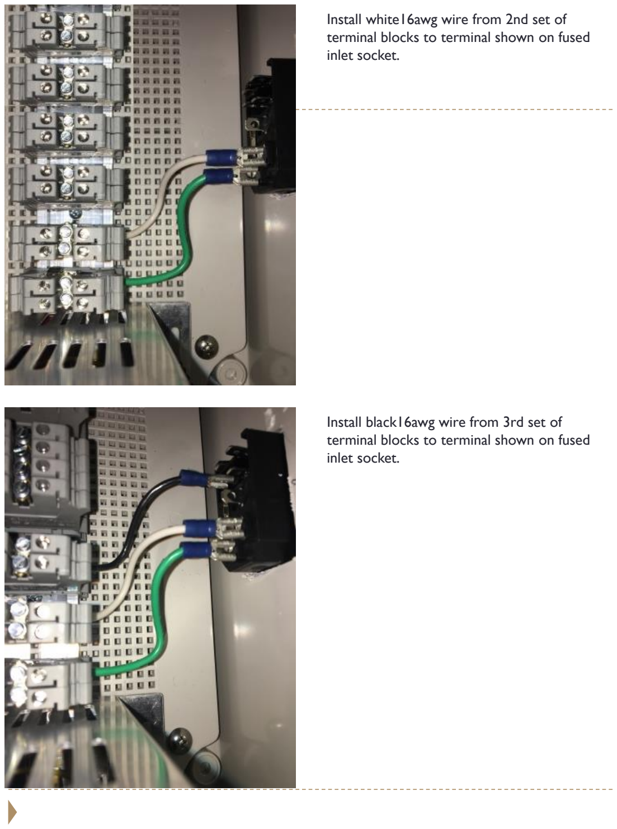
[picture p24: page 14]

Install black16awg wire from 3rd set of terminal blocks to terminal shown on fused inlet socket.

Install white16awg wire from 2nd set of terminal blocks to terminal shown on fused inlet socket.

Install black 16awg wire from 3rd terminal block from bottom to the Line terminal on power supply.

Install jumper as shown on inlet socket.

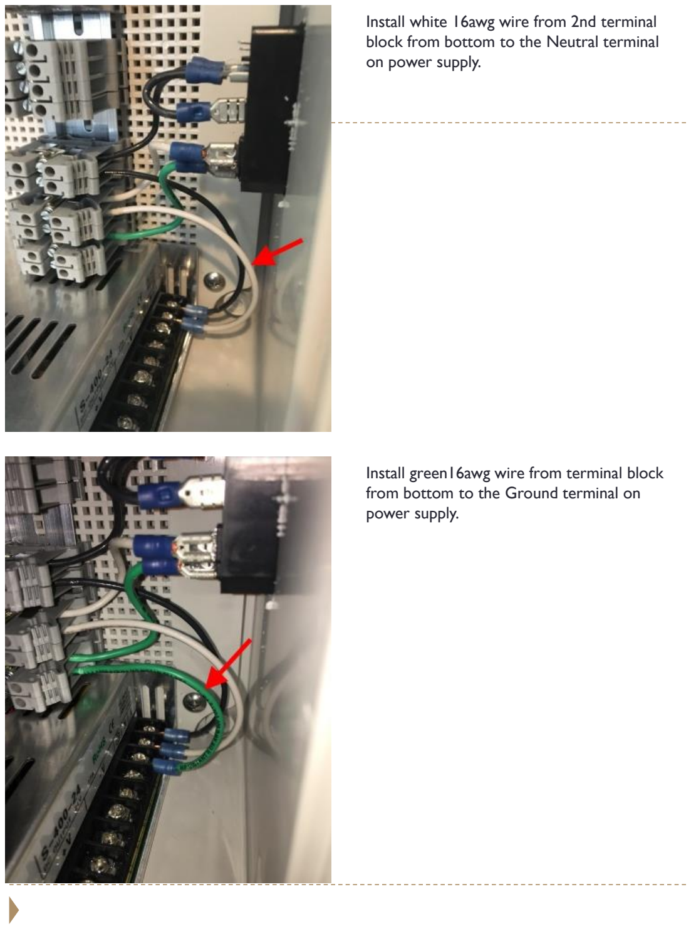
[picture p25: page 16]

Install green16awg wire from terminal block from bottom to the Ground terminal on power supply.

Install white 16awg wire from 2nd terminal block from bottom to the Neutral terminal on power supply.

Use stepped drill bit to drill ½” diameter hole on left side of enclosure 1.5” from top. Drill 7/8” hole 2” down from ½” hole and then another 7/8” hole 5” down from the first 7/8” hole.

Install blue 16 awg wire from the 4th from the bottom terminal block to the DC-terminal on bottom stepper driver and then install jumpers all the way up across all 6 drivers.

Install brown 16 awg wire from the 5

th from
the bottom terminal block to the DC+ terminal on bottom stepper driver and then install jumpers all the way up across all 6 drivers.

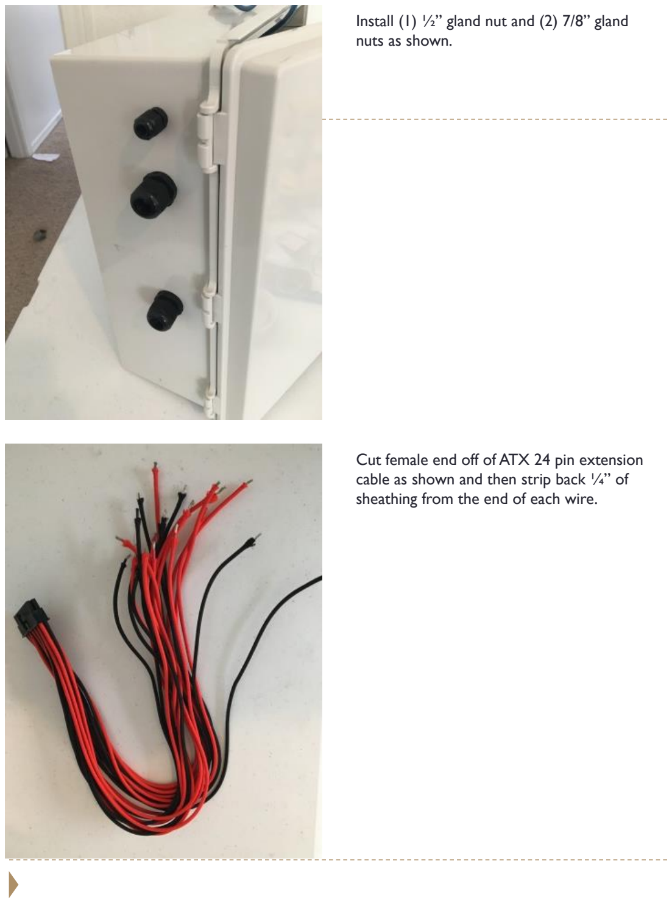
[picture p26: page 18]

Cut female end off of ATX 24 pin extension cable as shown and then strip back ¼” of sheathing from the end of each wire.

Install (1) ½” gland nut and (2) 7/8” gland nuts as shown.

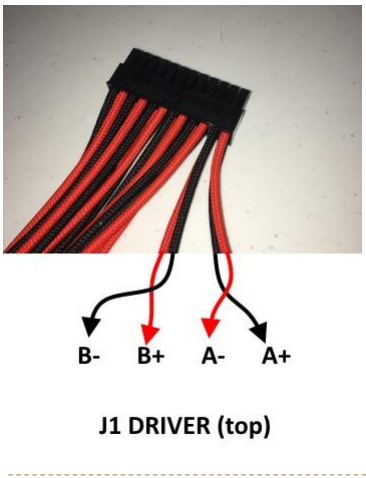
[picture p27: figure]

The next step is to land the ATX extension wires to the correct terminal on all 6 drivers. This and the following 5 slides will illustrate which wires go to the correct driver terminals. You will need to trace each wire inside the enclosure and connect as shown. The top driver in the enclosure is for J1 the second down is for J2 and down on. Also refer to the full wiring diagram at the end of this manual as well as the ATX pinout diagram.

Connect the J1 driver to the wires shown

(note the male connector tab is on top in the picuture)

With ATX male end clip facing out toward you as shown insert the top 12 wires into the top gland nut and then insert the bottom 12 wires into the bottom gland nut.

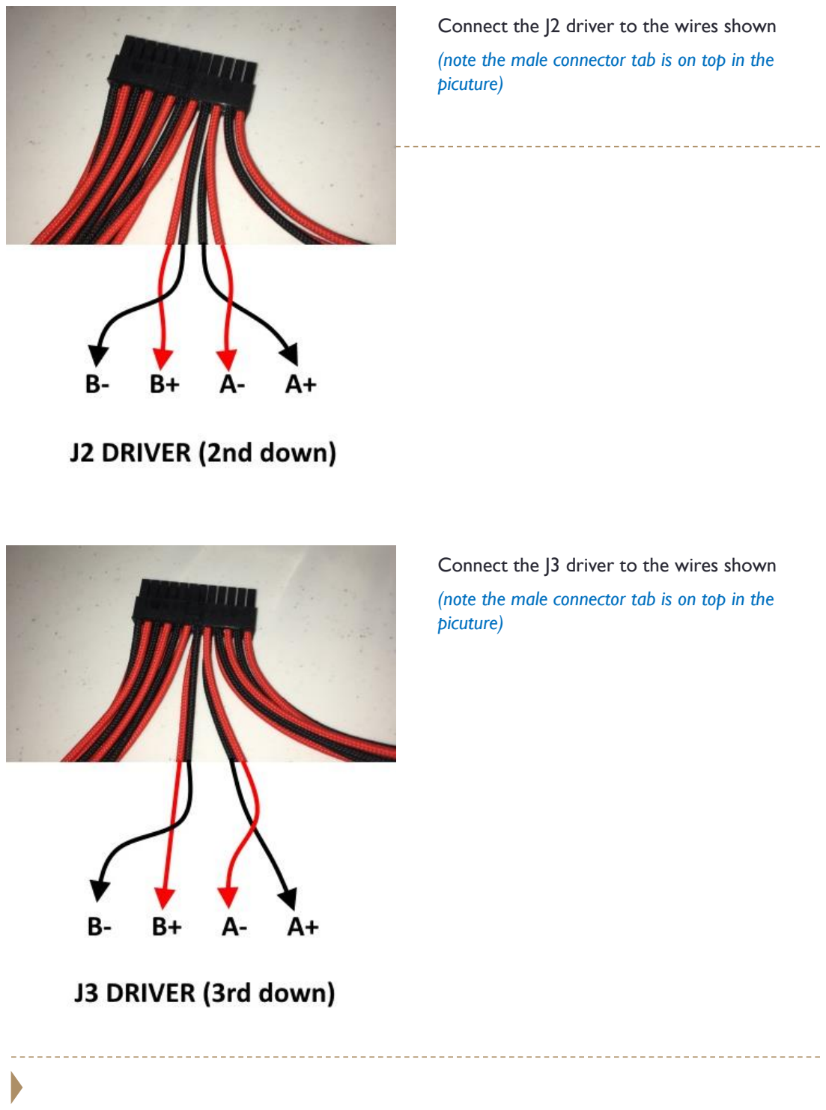
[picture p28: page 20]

Connect the J3 driver to the wires shown

(note the male connector tab is on top in the picuture)

Connect the J2 driver to the wires shown

(note the male connector tab is on top in the picuture)

Connect the J5 driver to the wires shown

(note the male connector tab is on top in the picuture)

Connect the J4 driver to the wires shown

(note the male connector tab is on top in the picuture)

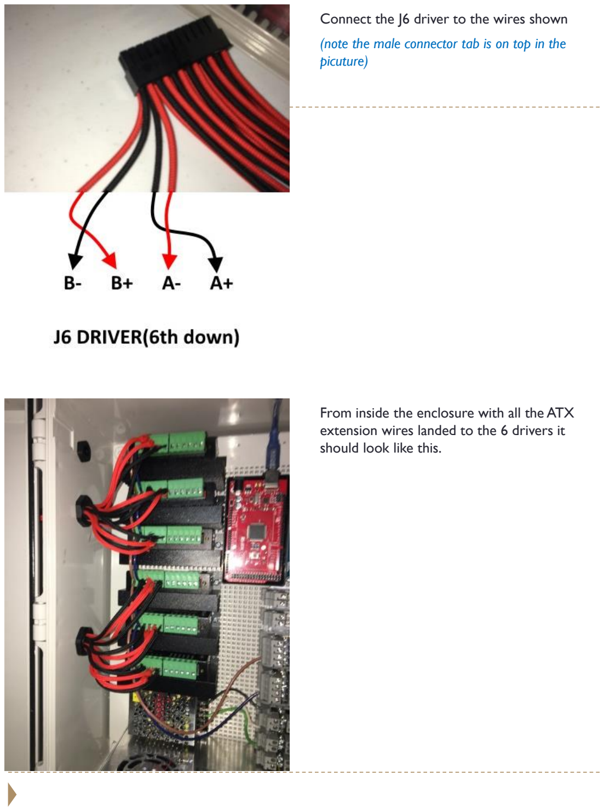
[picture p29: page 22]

From inside the enclosure with all the ATX extension wires landed to the 6 drivers it should look like this.

Connect the J6 driver to the wires shown

(note the male connector tab is on top in the picuture)

- For the next step you will need to jumper +5vdc across all +driver terminals. Use 15 short red jumpers and one long red jumper - twist ends together end to end so you have a chain of jumpers. Test continuity across all jumpers before installing.

(Also refer to the full wiring diagram at the end of this manual )

Trace the circle from the vent onto front cover door, cut out circle and mount vent in front of stepper drivers as shown.

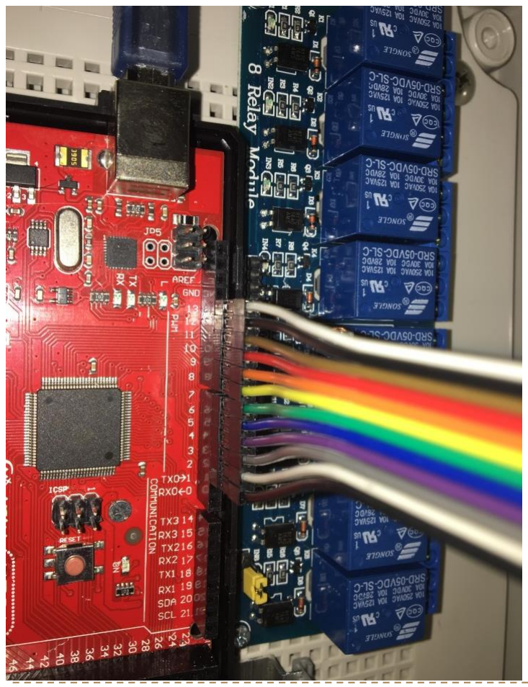
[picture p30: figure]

Connect a ribbon of (12) jumper wires to pins 2 through 13 on the arduino board as follows:

- Pin 2 to black to J1 PUL(-5)
- Pin 3 to white to J1 DIR(-5)
- Pin 4 to grey to J2 PUL(-5)
- Pin 5 to purple to J2 DIR(-5)
- Pin 6 to blue to J3 PUL(-5)
- Pin 7 to green to J3 DIR(-5)
- Pin 8 to yellow to J4 PUL(-5)
- Pin 9 to orange to J4 DIR(-5)
- Pin 10 to red to J5 PUL(-5)
- Pin 11 to brown to J5 DIR(-5)
- Pin 12 to black to J6 PUL(-5)
- Pin 13 to white to J6 DIR(-5)

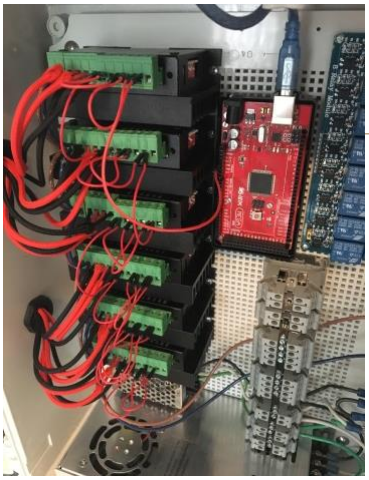
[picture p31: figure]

The next step is to run 5vdc from the arduino to all the (+5v) terminals across all of the stepper drivers. The drivers are NPN or negative switching which means the step and direction pulses will be made by the negative wire and the positive is high or on all the time on all the (+5v) terminals. Each driver has (3) positive terminals that require a constant +5v signal:

- PUL+(+5)
- DIR+(+5)
- ENA+(+5)

Run a long jumper from the arduino +5v to the J1 stepper drivers ENA+(+5v) terminal, then jumper that over to the DIR+(+5) and jumper that over to the PUL+(+5), then jumper to the next driver and across its (3) (+5) terminals and continue down and across all drivers – you will need a total of (17) short jumper wires.

(Also refer to the full wiring diagram at the end of this manual )

Connect a long blue jumper from the top set of terminal blocks over to the ENA-(ENA) on the J6 driver and then use 5 short blue jumpers to jump across the ENA-(ENA) on all stepper drivers. The purpose of these wires is to disable all the stepper drivers. If you were to provide a negative input to any of the other 3 inputs on the top set of terminal blocks this would disable all drivers. This circuit will not be used any further in this manual but its purpose would be if you had a safety switch or gate protecting your robot you would wire your safety gate to these terminals to provide -5v when the gate is open and this will disable any motors while the gate or safety circuit is open.

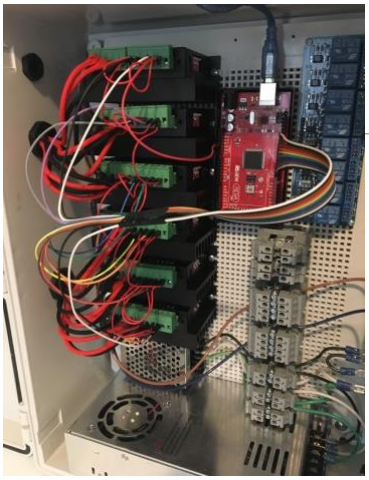
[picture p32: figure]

Extend the jumper wires with matching color wires and connect to the stepper drivers negative pulse and direction terminals as outlined in the previous step.

(Also refer to the full wiring diagram at the end of this manual )

Install USB (B) to (A) panel jack as shown.

Use stepped drill bit to drill a 7/8” hole in right side of enclosure centered in panel toward the top of enclosure as shown.

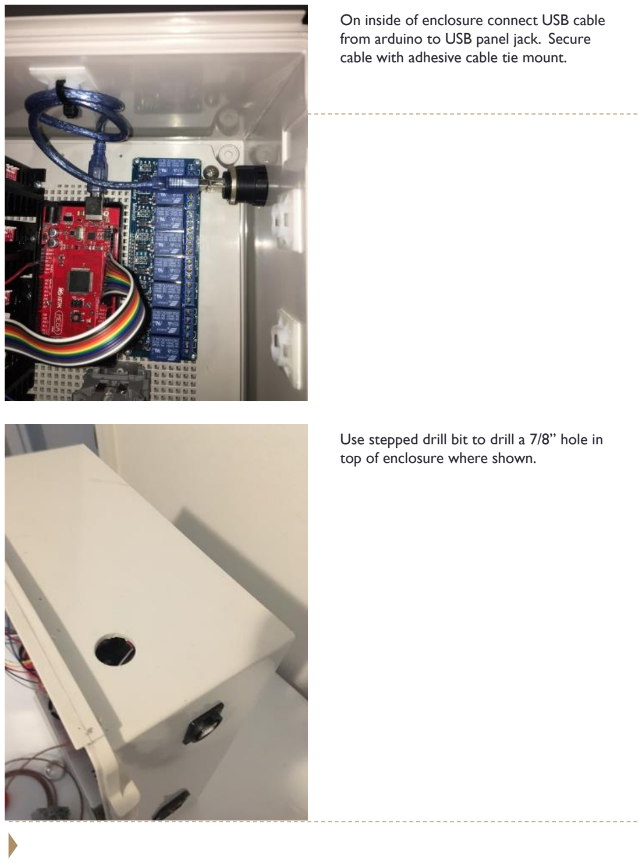
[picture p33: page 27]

Use stepped drill bit to drill a 7/8” hole in top of enclosure where shown.

On inside of enclosure connect USB cable from arduino to USB panel jack. Secure cable with adhesive cable tie mount.

Connect brown 16awg wire from +V terminal on 24vdc power supply up to terminal on E-Stop switch – then from opposite terminal on E-Stop switch down to the 5th from the bottom terminal block group on DIN rail.

The E-Stop button will cut off the 24vdc power to the stepper drivers.

Install E-Stop button as shown.

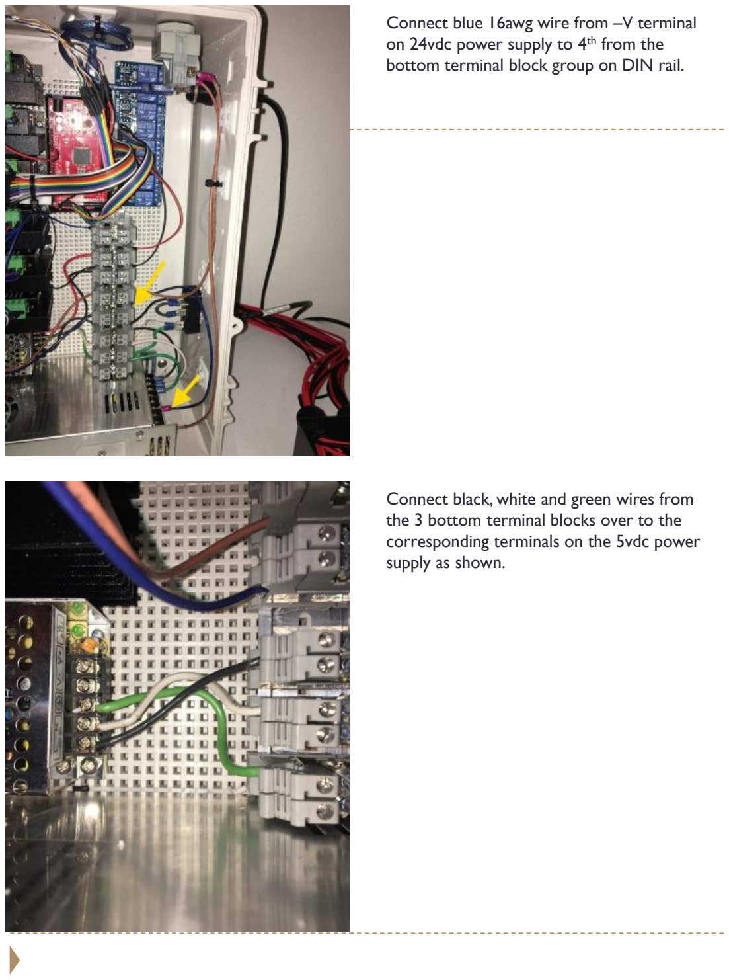
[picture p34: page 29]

Connect black, white and green wires from the 3 bottom terminal blocks over to the corresponding terminals on the 5vdc power supply as shown.

Connect blue 16awg wire from –V terminal on 24vdc power supply to 4th from the bottom terminal block group on DIN rail.

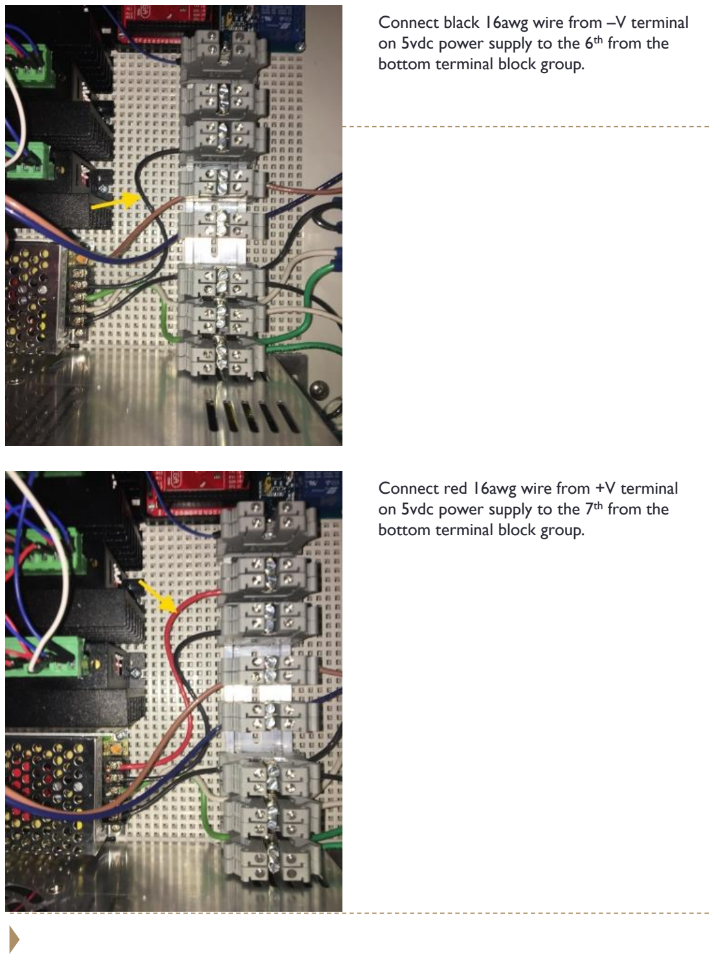
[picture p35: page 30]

Connect red 16awg wire from +V terminal on 5vdc power supply to the 7

th from the
bottom terminal block group.

Connect black 16awg wire from –V terminal on 5vdc power supply to the 6th from the bottom terminal block group.

This photo shown the other end of the ribbon connected to pins 38 through 45 on the arduino.

Connect a ribbon of (8) wires from the 8 channel relay board to the arduino as follows:

- IN1 to black to arduino pin 38
- IN2 to white to arduino pin 39
- IN3 to grey to arduino pin 40
- IN4 to purple to arduino pin 41
- IN5 to blue to arduino pin 42
- IN6 to green to arduino pin 43
- IN7 to yellow to arduino pin 44
- IN8 to orange to arduino pin 45

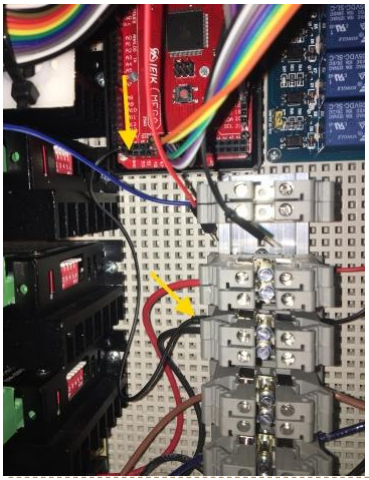
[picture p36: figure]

Connect a long black jumper from the far bottom left GND terminal on the arduino to the -5vdc terminal group on the DIN rail (6th from the bottom)

The arduino and the 5vdc power supply must share ground connection – the 5vdc supply powers the relays as the arduino tends to run short on power.

Connect a long red jumper from the VCC terminal on the relay board to the +5vdc terminal blocks on the DIN rail (7th from the bottom)

Connect a long black jumper from the GND terminal on the relay board to the -5vdc terminal blocks on the DIN rail (6th from the bottom)

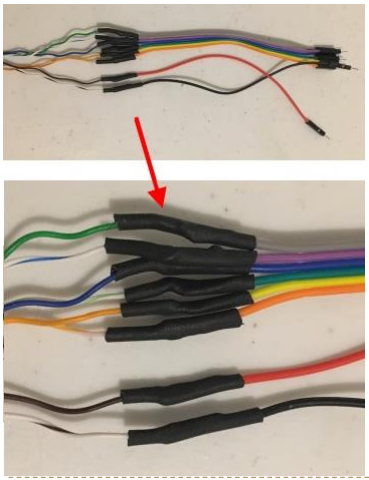
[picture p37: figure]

Solder and heat shrink tube a (6) ribbon set of jumpers as follows:

- RJ45 white/or stripe to orange to arduino pin 14
- RJ45 or/white stripe to yellow to arduino pin 15
- RJ45 white/gr stripe to green to arduino pin 16
- RJ45 blue/white stripe to blue to arduino pin 17
- RJ45 white/blue stripe to purple to arduino pin 18
- RJ45 green/white stripe to grey to arduino pin 19

Then connect:

- RJ45 brown/wh stripe to red jumper to arduino +5v
- RJ45 white/brown stripe to black jumper to arduino GND

Cut off the male end of an RJ45 extension cable, remove 2” of outer sheathing then strip ¼” sheathing off each individual wire.

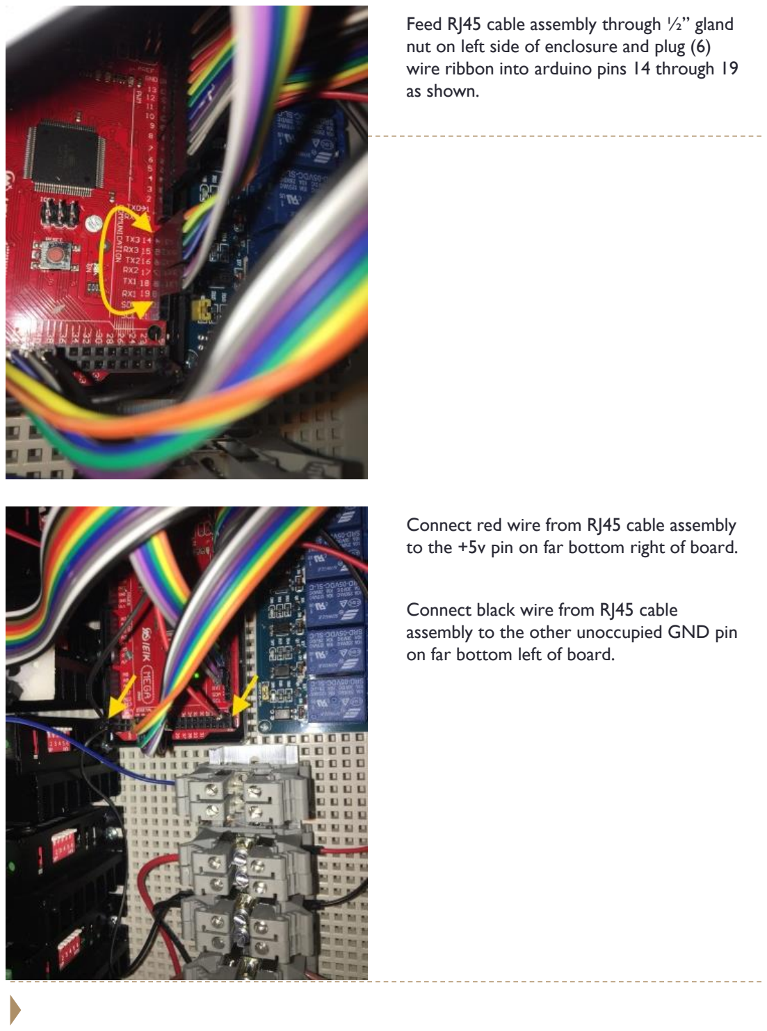
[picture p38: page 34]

Connect red wire from RJ45 cable assembly to the +5v pin on far bottom right of board.

Connect black wire from RJ45 cable assembly to the other unoccupied GND pin on far bottom left of board.

Feed RJ45 cable assembly through ½” gland nut on left side of enclosure and plug (6) wire ribbon into arduino pins 14 through 19 as shown.

# COMPLETED LAYOUT

## THIS PHOTO SHOWS THE COMPLETED LAYOUT USING THE

## UPDATED (5) DM542T & (1) DM320T DRIVER

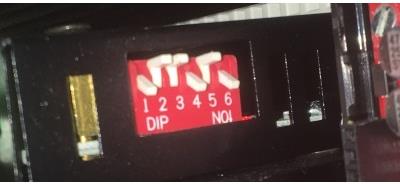
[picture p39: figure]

Set the dip switches for J2 stepper driver:

J2= ¼ step – 3amp
Switch 1 – down
Switch 2 – up
Switch 3 – up
Switch 4 – down
Switch 5 – up
Switch 6 – down

Set the dip switches for J1 stepper driver:

J1= ¼ step – 1.5amp
Switch 1 – down
Switch 2 – up
Switch 3 – up
Switch 4 – up
Switch 5 – down
Switch 6 – up

## DIP SWITCH SETTING USING ST-6600 DRIVERS AND ECONOMY SERIES GEARDRIVE MOTORS (original configuration)

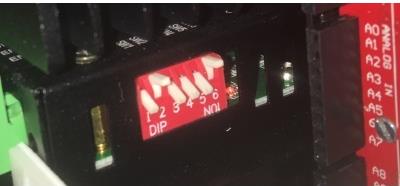
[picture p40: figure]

Set the dip switches for J3 stepper driver:

J3= 1/8 step 2amp
Switch 1 – down
Switch 2 – up
Switch 3 – down
Switch 4 – down
Switch 5 – down
Switch 6 – up

THESE SETTINGS ARE USED FOR THE FOLLOWING ECONOMY SERIES MOTORS:
- J1 - 17HS19-1684S-PG5 | 1/4 STEPS | 1.5 AMP
- J2 - 23HS30-2804S-PG47 | 1/4 STEPS | 3 AMP
- J3 - 17HS19-1684S-PG19 | 1/8 STEPS | 2 AMP
- J4 - 11HS20-06742-PG5 | 1/2 STEPS | 1 AMP
- J5 - 17LS19-1684E-200G | 1/4 STEPS | 1.5 AMP
- J6 - 14HS13-0804S-PG19 | 1/4 STEPS | 1 AMP

Set the dip switches for J6 stepper driver:

J6= ¼ step – 1amp
Switch 1 – down
Switch 2 – up
Switch 3 – up
Switch 4 – down
Switch 5 – up
Switch 6 – up

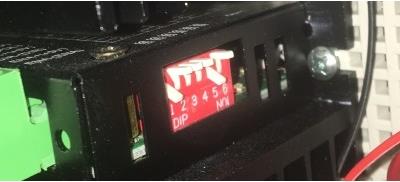
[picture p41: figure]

Set the dip switches for J5 stepper driver:

J5= ¼ step – 1.5amp
Switch 1 – down
Switch 2 – up
Switch 3 – up
Switch 4 – up
Switch 5 – down
Switch 6 – up

Set the dip switches for J4 stepper driver:

J4= ½ step – 1amp
Switch 1 – up
Switch 2 – down
Switch 3 – up
Switch 4 – down
Switch 5 – up
Switch 6 – up

## UPDATED DIP SWITCH SETTING USING DM542T DRIVERS (J1,J2,J3,J5,J6) - DM320T - (J4) WITH 3 PRECISION & 3 ECONOMY SERIES GEARDRIVE MOTORS (recommended)

THESE SETTINGS ARE USED FOR THE FOLLOWING SERIES MOTORS: (J1,J2 &J3 are precision series J4,J5 & J6 are economy series)

- J1 - 17HS15-1684S-HG20 | 1/4 STEPS | 1.46 AMP
- J2 - 23HS22-2804S-HG50 | 1/4 STEPS | 2.37 AMP
- J3 - 17HS15-1684S-HG50 | 1/4 STEPS | 1.46 AMP
- J4 - 11HS20-06742-PG5 | 1/4 STEPS | .5 AMP
- J5 - 17LS19-1684E-200G | 1/4 STEPS | 1.46 AMP
- J6 - 14HS13-0804S-PG19 | 1/4 STEPS | 1 AMP

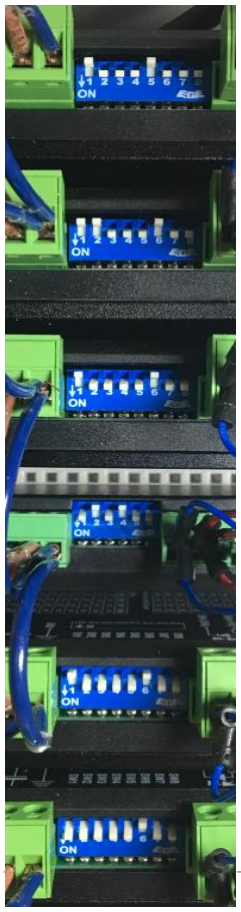
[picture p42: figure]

J1 – (DM542T):
SW1 = OFF SW2 = ON | SW3 = ON | SW4 = ON
SW5 = OFF SW6 = ON | SW7 = ON | SW8 = ON

J2 – (DM542T):
SW1 = OFF SW2 = OFF SW3 = ON | SW4 = ON
SW5 = ON | SW6 = OFF SW7 = ON | SW8 = ON

J3 – (DM542T):
SW1 = OFF SW2 = ON | SW3 = ON | SW4 = ON
SW5 = ON | SW6 = OFF SW7 = ON | SW8 = ON

J4 – (DM320T):
SW1 = ON | SW2 = OFF SW3 = ON
SW4 = OFF SW5 = ON | SW6 = ON

J5 – (DM542T):
SW1 = OFF SW2 = ON | SW3 = ON | SW4 = ON
SW5 = ON | SW6 = OFF SW7 = ON | SW8 = ON

J6 – (DM542T):
SW1 = ON | SW2 = ON | SW3 = ON | SW4 = ON
SW5 = ON | SW6 = OFF SW7 = ON | SW8 = ON

39

# Startup

40

### - I would recommend making a wiring harness per the wiring harness manual from the project page. If you are direct wiring per this 3D printed robot assembly manual I recommend waiting to loom all the wires on the robot until after you have started up the robot so you can make sure all axis fully

articulate and you have plenty of slack on the wires.

### - Load the “sketch_Annin_Robot.ino” to the arduino and take note which COM

port your arduino is connected to.

### - Before opening the AR2 software and establishing a serial connection toggle

each limit switch on the robot and make the the LED on the arduino lights up.

### Every switch should make the LED come on its imperative these all work

otherwise you cannot calibrate the robot.

### - Open the AR2 software and set the COM port (you should only have to do this the first time)

- Carefully test each axis – jog J1 through J6 a couple degrees (be careful – robot is not calibrated yet and you can drive an axis too far and bend one of your switches) in each direction to make sure you can jog in each direction. If you find an axis not moving or if the + and – jog buttons make the axis go in the same direction then you very likely have an issue with the step or direction wires to the stepper drivers or an issue with one of the many jumpers. I have found every problem I have encountered has been due to a jumper not making connection or coming loose. I cant stress enough the need to secure each wire and check with a meter. If you hit axis limits when testing before you have calibrated you can press the “Force Calibration to Mid Range” button and this will set your current calibration to mid point and allow you to jog – but be careful this button is only for testing to allow you to get around axis limits

before you calibrate.

### - Note different drivers can rotate the motors in different directions; in the arduino sketch near the top of the program you can change the motor direction values. If using DM542T driver(CW) set to 0 // if using ST6600

driver(CCW) set to 1 then load then reload the sketch.

### - Press the auto calibrate button – the robot should move to each limit switch

and calibrate each axis to its limit.

### SETUP VIDEO: https://youtu.be/MMESgfq2Mjg

### PROGRAMMING VIDEO: https://youtu.be/BozgdjE-HR8

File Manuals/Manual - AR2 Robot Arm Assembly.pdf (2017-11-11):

# Model AR2 Assembly Manual

## MECHANICAL UNIT ASSEMBLY

1 | Mechanical Unit Assembly Manual

NOTE:
Currently the primary differences between the aluminum version and the printed version are as follows:
- The aluminum version uses precision series motors for J1, J2 and J3:
- J1 = SKU: 17HS15-1684S-HG5
- J2 = SKU: 23HS22-2804S-HG50
- J3 = SKU: 17HS15-1684S-HG50
(the printed version uses economy series motors as shown in the bill of materials)
- The aluminum version uses different motor mounts for J1 & J3.
- The aluminum version uses a different spindle and tension plate for J2.
- The spindle and plate for the aluminum (precision motors) have a 14mm bore.
- The spindle and plate for the printed (economy motors) have a 12mm bore.
- The aluminum version uses a slightly different motor support for J2.
- The bore for the aluminum version is 1mm larger, has a split in the ring for clamping onto the motor body and it does not have the extension and hole for the spring dampener.
- The aluminum version does not use the spring dampener components.
- The aluminum version uses DM542T and DM320T digital stepper drivers.
- The printed version uses analog ST6600 drivers.
- The aluminum version uses only the chain drive for J3.
- The aluminum version uses the wiring harness as outlined in the wiring harness manual on the project page.

The aluminum and printed version can be constructed either way – (using precision or economy motors). Both sets of models (.step files for the aluminum version and the .stl files for the printed version) are included in both sets of models to accommodate the differences listed above. The files for use with the precision series motors have the suffix “- precision GB”. In the next few months I will be creating a new manual showing the robots construction using aluminum components and the precision gearboxes. At that time I will archive the current manual replacing it with the new manual and obsolete the current instructions using the economy components. The design going forward will be using only the precision series motors and the digital drivers as these are far superior for a relatively minor increase in cost. The current manual can be used for constructing the aluminum version given the changes outlined above.

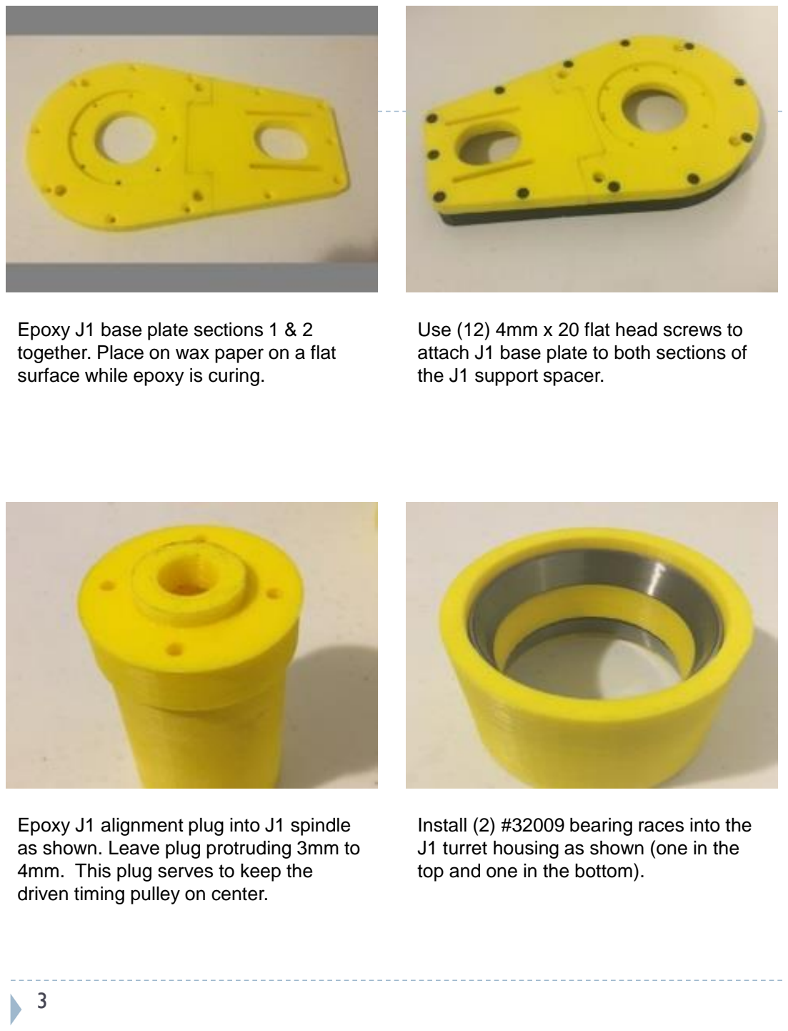
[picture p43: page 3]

Epoxy J1 base plate sections 1 & 2 together. Place on wax paper on a flat surface while epoxy is curing.

Use (12) 4mm x 20 flat head screws to attach J1 base plate to both sections of the J1 support spacer.

Epoxy J1 alignment plug into J1 spindle as shown. Leave plug protruding 3mm to 4mm. This plug serves to keep the driven timing pulley on center.

Install (2) #32009 bearing races into the J1 turret housing as shown (one in the top and one in the bottom).

Install #32009 bearings on J1 spindle. | Place the J1 spindle and bearing into the bottom of the J1 housing.

Flip the housing assembly over and place the 2nd #32009 bearing over the other side of the spindle as shown.

Install (2) #30206 bearing races into the J2 turret housing as shown.

Attach the J2 turret housing to the J1 platform using (6) M6 x 18 flat head screws.

Install (2) M6 x 14 socket head screws in front of J2 turret housing going into the J1 platform.

Use an abrasive cut off disc and cut (1) M8 x 25 square head set screw down to 20mm total length.

Install M8 square head screw in J1 baseplate as shown. Square head should be tangent to J1 rotation (the head is the contact for the J1 limit switch).

Install platform assembly onto J1 spindle assembly and secure with (8) M6 X 14 socket head cap screws.

Install (4) M4 x 10 set screws in the 4 perimeter holes in the platform. These place tension on the upper bearing. Snug the 4 set screws down evenly until there is no play in the bearings.

Install the J1 assembly onto the base assembly as shown. Make sure the flat surface with 2 holes is facing toward the back.

Secure J1 assembly from the bottom using (8) M4 X 10 socket head cap screws.

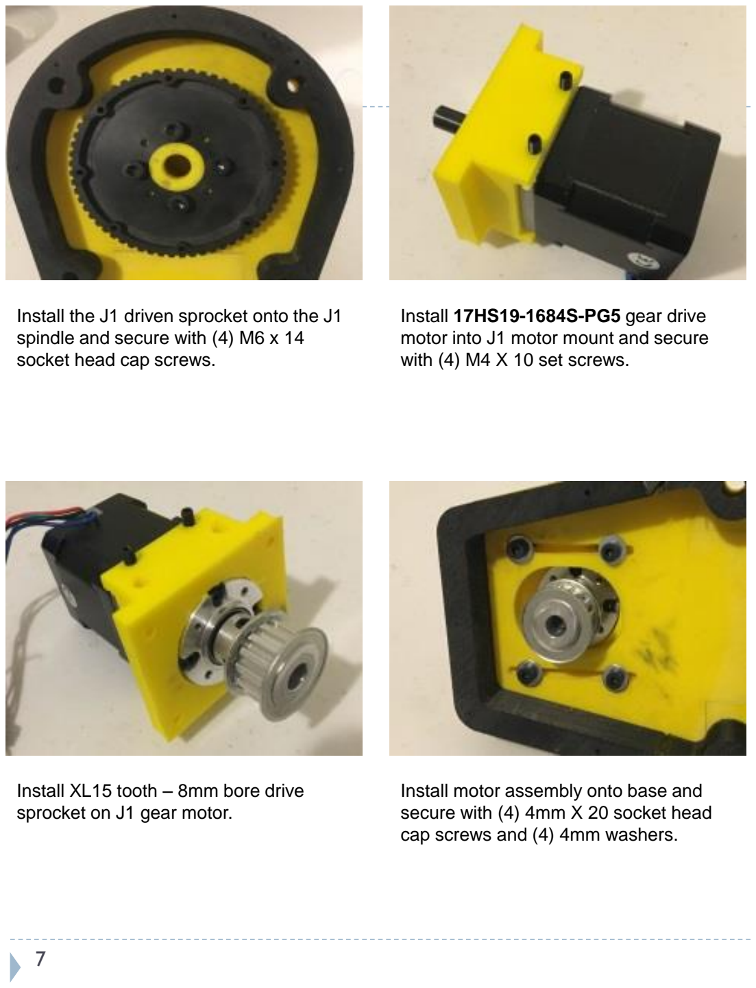
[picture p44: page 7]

Install the J1 driven sprocket onto the J1 spindle and secure with (4) M6 x 14 socket head cap screws.

Install 17HS19-1684S-PG5 gear drive motor into J1 motor mount and secure with (4) M4 X 10 set screws.

Install XL15 tooth – 8mm bore drive sprocket on J1 gear motor.

Install motor assembly onto base and secure with (4) 4mm X 20 socket head cap screws and (4) 4mm washers.

Install 180XL37 timing belt, set tension and tighten motor mount screws.

Connect a black, red, and yellow 22awg with .187” quick disconnect wire to limit switch as shown.

Mount limit switch to J1 housing using M3 X 14 socket head cap screw.

Use epoxy to glue the 1st of 6 support braces on left side of base with corner aligned with screw head as shown. Note: support braces are not required for aluminum robot.

Epoxy 2nd support brace in place 7mm from the next screw head.

Epoxy 3rd support brace centered between next pair of screw heads.

Epoxy the 4th 5

th and 6th support braces
on opposite side mirror image to the first side.

Drill (2) 8mm holes 12mm from bottom 32mm apart.
Drill (2) 6mm holes 22mm from bottom 22mm apart
In 6” x 3” plastic enclosure as shown.

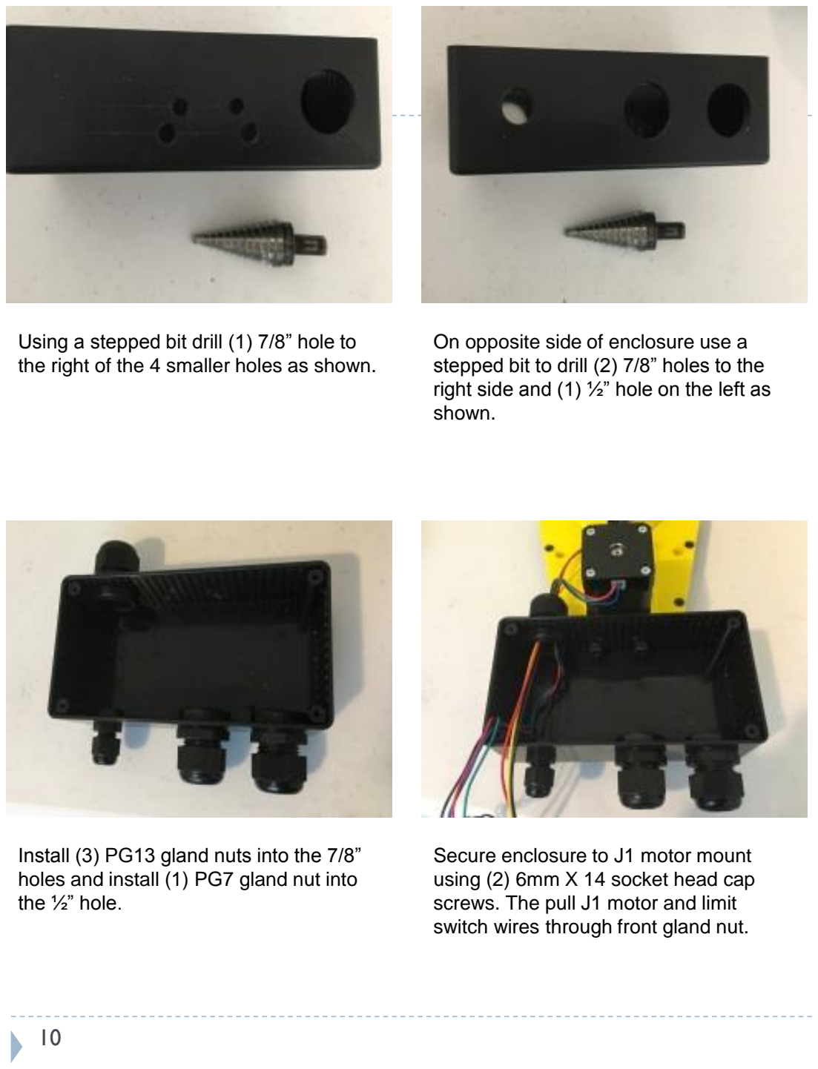
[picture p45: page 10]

Using a stepped bit drill (1) 7/8” hole to the right of the 4 smaller holes as shown.

On opposite side of enclosure use a stepped bit to drill (2) 7/8” holes to the right side and (1) ½” hole on the left as shown.

Install (3) PG13 gland nuts into the 7/8” holes and install (1) PG7 gland nut into the ½” hole.

Secure enclosure to J1 motor mount using (2) 6mm X 14 socket head cap screws. The pull J1 motor and limit switch wires through front gland nut.

Cut the male connector off of one ATX 24 pin extension cable and then strip ¼” of sheathing off the end of each wire.

Insert 12 wires from the left side and 12 wires from the right side of the ATX 24 pin extension into the left and right PG13 gland nuts respectively.

Cut the male connector off of one RJ45 extension cable, strip back 2” of the outer black sheathing and then strip ¼” of sheathing off the end of each wire.

Insert the RJ45 extension cable into the PG7 gland nut as shown.

(The next 5 steps will outline connecting wires using solder and heat shrink tubing) We will start with the red wire from the J1 limit switch going to the brown wire on the RJ45 cable - Slip a piece of heat shrink tube over the red wire.

Twist the ends of the red wire from the J1 limit switch to the brown wire from the RJ45 cable.

Use a soldering iron and rosin core silver bearing solder to solder the wires together.

Bend the brown wire away from the solder joint as shown.

Pull the heat shrink tube down over the solder joint and then use a heat gun or soft flame to shrink the tube over the joint. (future steps in this manual will not go into detail on soldering but will only state to solder and heat shrink over the connection).

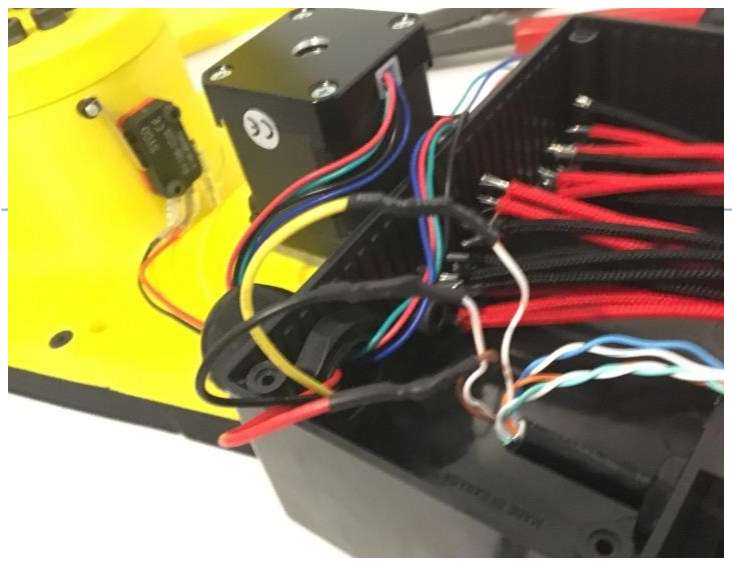
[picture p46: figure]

Use solder and shrink tubing to connect the J1 limit switch black to the white/brown stripe on RJ45. Connect the J1 limit switch yellow to the white/orange stripe on the RJ45.

(Also refer to the RJ45 pinout diagram and the limit switch schematic).

The next step is to connect the (4) J1 motor wires to the correct wires on the ATX cable. You will need to trace the wires from the back of the connector and find the end inside the enclosure.

(Also refer to the ATX pinout diagram and the stepper motor wiring schematic)

Solder and heat shrink the following connections:
- ATX pin 1 to J1 black
- ATX pin 2 to J1 red
- ATX pin 13 to J1 green
- ATX pin 14 to J1 blue

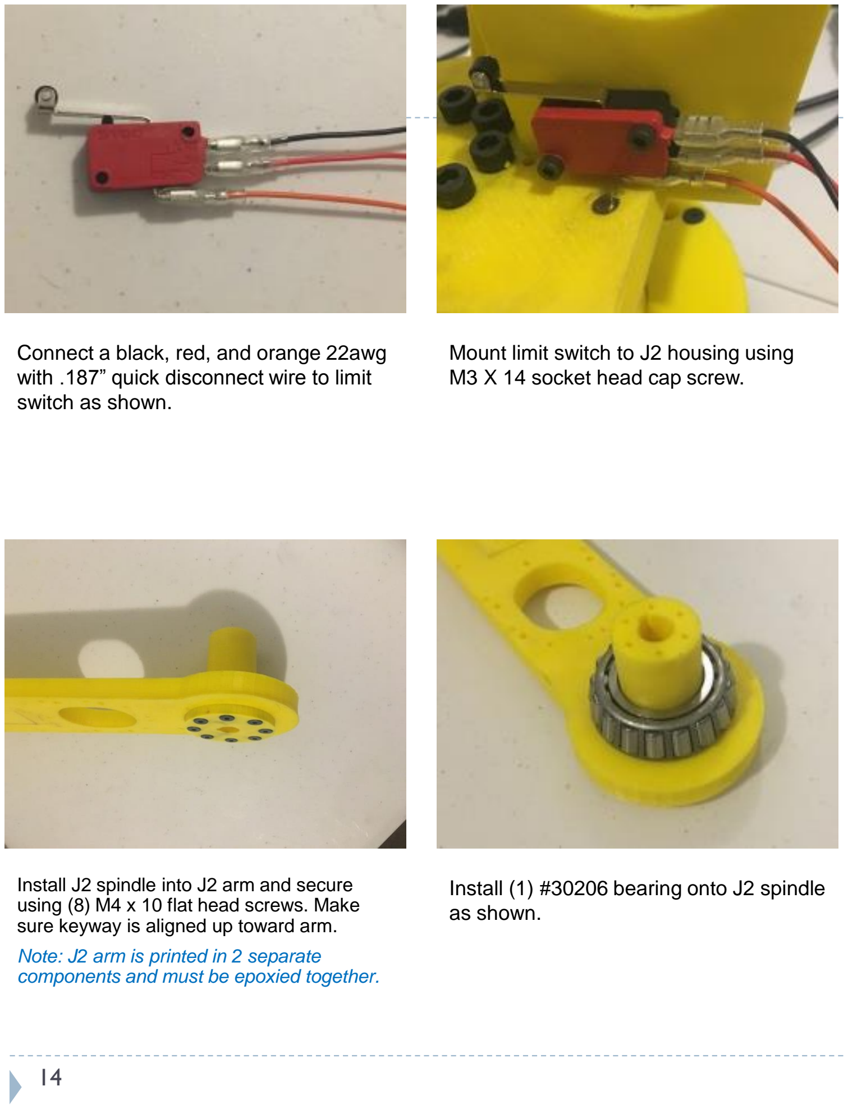
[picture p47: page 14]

Connect a black, red, and orange 22awg with .187” quick disconnect wire to limit switch as shown.

Mount limit switch to J2 housing using M3 X 14 socket head cap screw.

Install J2 spindle into J2 arm and secure using (8) M4 x 10 flat head screws. Make sure keyway is aligned up toward arm. Note: J2 arm is printed in 2 separate components and must be epoxied together.

Install (1) #30206 bearing onto J2 spindle as shown.

Pre install (1) M3 x 6 set screw in J2 spindle but do not allow it to protrude into keyway yet.

Install J2 arm assembly as shown and then install the other #30206 bearing from the opposite side.

Apply a liberal amount of epoxy into end of J2 spindle retainer and Install M8 – T nut as shown.

After epoxy is cured sand excess epoxy both front and back as well as the bottom to make sure all sides are flush.

Install the J2 spindle retainer and secure with (6) M3 x 25 flat head screws. Snug screws until there is no play in J2 bearings.

Install M6 ball joint. Grind 1 to 2 threads off post - do not allow threads to extend out other side of retainer.

Install J2 motor motor support plate using (3) M6 x 18 flat head screws.

Install auxiliary spring housing support. Secure in place with (3) M4 x 10 socket head screws – in addition to screws apply epoxy between support and J2 turret housing.

Grind 2 threads from end of M8 x 14 shoulder screws so that threads do not extend inside spring housing.

Install spring housing and secure with (2) M8 x 14 shoulder screws. Apply grease inside mounting holes – make sure spring housing rotates freely.

Install M8 x 80 shoulder screw through spring plunger then place (1) 2” x .845” x .080” spring and (1) 3” x .56” x .054” spring over shoulder screw.

Install spring assembly into spring housing and extend shoulder screw through end of spring housing and screw into the ball linkage.

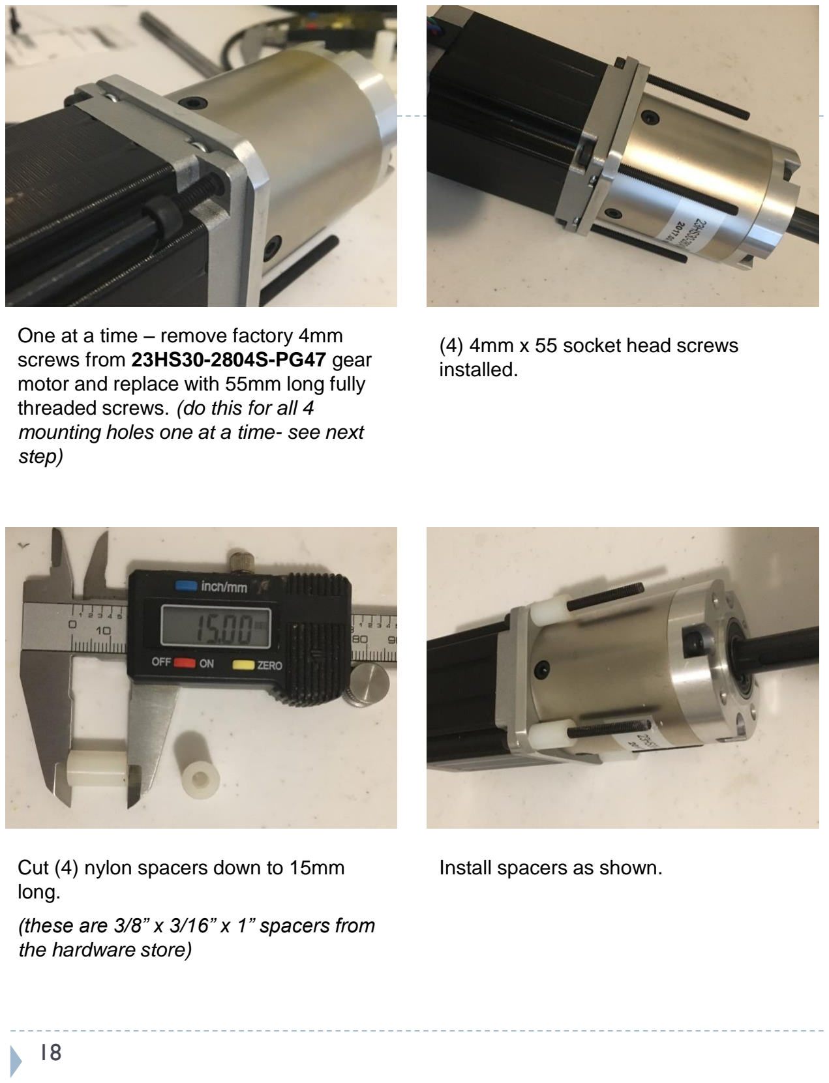
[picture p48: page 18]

One at a time – remove factory 4mm screws from 23HS30-2804S-PG47 gear motor and replace with 55mm long fully threaded screws. (do this for all 4 mounting holes one at a time- see next step)

(4) 4mm x 55 socket head screws installed.

Cut (4) nylon spacers down to 15mm long.

(these are 3/8” x 3/16” x 1” spacers from the hardware store)

Install spacers as shown.

Install 23HS30-2804S-PG47 gear motor as shown and secure with (4) 4mm washers and nuts.

Make sure keyway in shaft and spindle are aligned.

Cut length of 4mm key stock down to 60mm length using abrasive saw.

Use belt sander to round the corners on one end.

Insert 4mm key as shown with rounded end in.

Use small hammer to lightly tap the key fully into position.

With J2 arm straight up tighten 3mm set screw onto key stock that was inserted.

Route J2 motor wires through hole in support plate as shown.

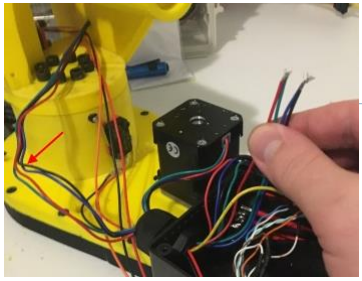
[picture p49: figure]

Pull the J2 wires into enclosure. Do not trim these wires they need to stay full length.

The next step is to connect the (4) J2 motor wires to the correct wires on the ATX cable. You will need to trace the wires from the back of the connector and find the end inside the enclosure.
(Also refer to the ATX pinout diagram and the stepper motor wiring schematic)

Solder and heat shrink the following connections:
- ATX pin 3 to J2 black
- ATX pin 4 to J2 red
- ATX pin 15 to J2 green
- ATX pin 16 to J2 blue

Pull the orange wire from the J2 limit switch into the enclosure. Make sure orange wire has the same amount of slack as the other J2 wires and is run along side of them. This wire loom must have enough slack for J1 to fully articulate in both directions.

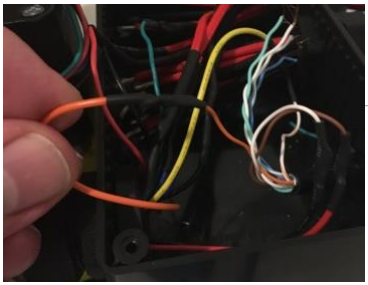
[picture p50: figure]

Use solder and shrink tubing to connect the J2 limit switch orange to the orange/white stripe on RJ45..
(Also refer to the RJ45 pinout diagram and the limit switch schematic).

Cut the red and black wires from the J1 limit switch as shown. (we need to splice power from these wires to the next J2 limit switch)

Strip ¼” of sheathing from each end of the wires you just cut.

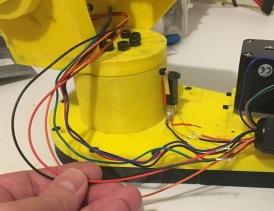
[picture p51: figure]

Cut and strip the red and back wires coming from the J2 limit switch. Make sure they have the same amount of slack as the other J2 wires and is run along side of them. This wire loom must have enough slack for J1 to fully articulate in both directions.

Place heat shrink tube over the red and black wires coming from the enclosure; then solder the back wires together and then the red wires together.

Pull the heat shrink tube over each of the 3 wire splices as shown and then apply heat to shrink the tube.

Install (1) 17HS19-1684S-PG19

geared stepper motor into J3 motor housing and secure with (6) M4 x 10 set screws. Then install (1) XL15 tooth – 8mm bore drive sprocket on motor shaft.

Note: there is also a chain option.

Install J3 motor assembly on J2 arm using (4) M4 x 20 socket head cap screws and (4) 4mm washers.

Install (1) #30204 bearing race into the J3 bearing cup.

Secure J3 bearing cup and race to end of J2 arm using (6) M3 x 25 flat head screws.

Use abrasive saw to cut length of 8mm keyed shaft to 53mm long.

Use abrasive saw to cut length of 2mm keyed stock to 25mm long

Install 8mm shaft into J3 spindle. Install 2mm key stock into shaft and spindle slot and secure with 3mm x 4 set screw.

Install 35x52x4 Thrust Bearing and washers onto J3 spindle.

Install J3 spindle and shaft into J2 arm, from opposite side slide #30204 bearing onto spindle shaft and install J3 spindle retainer. Secure with (4) M3 x 10 flat head screws. Tension screws so there is no play in bearings.

Install (1) XL15 tooth – 8mm bore drive pulley on J3 spindle shaft.

NOTE: these steps utilize XL series pulleys and belt to drive J3. following this there will be an option to use a 4mm roller chain instead.

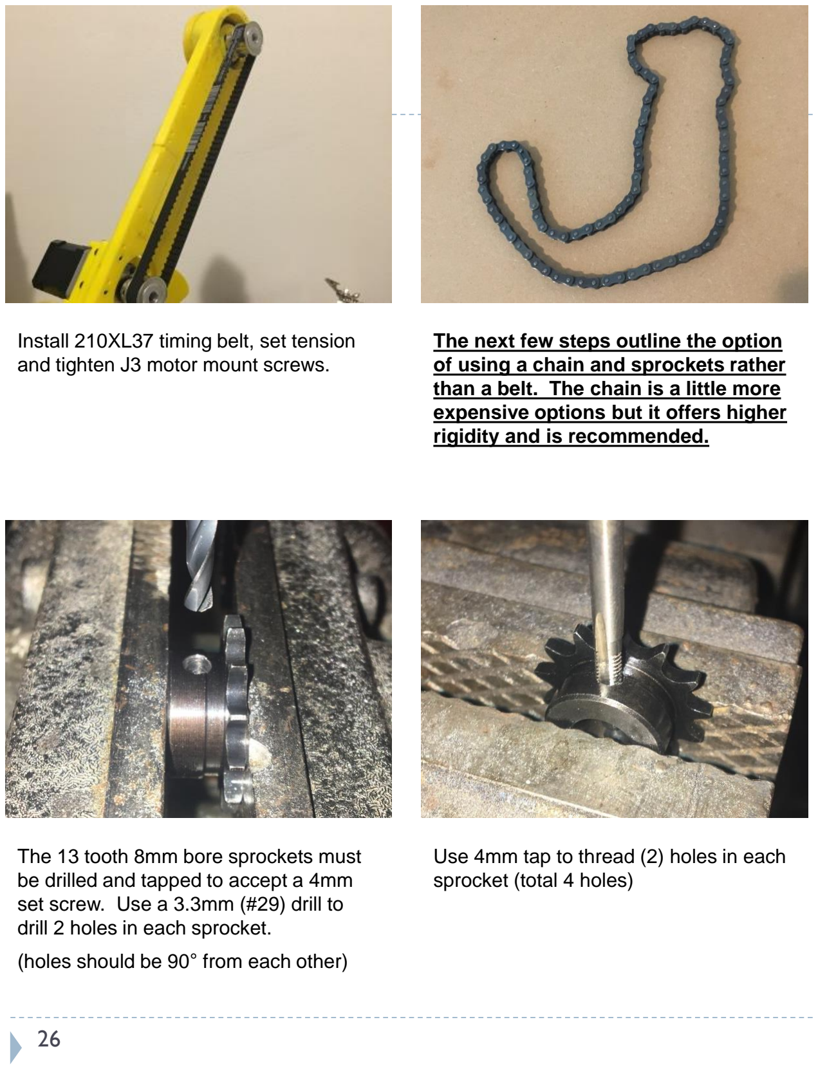
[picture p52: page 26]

Install 210XL37 timing belt, set tension and tighten J3 motor mount screws.

The next few steps outline the option of using a chain and sprockets rather than a belt. The chain is a little more expensive options but it offers higher rigidity and is recommended.

The 13 tooth 8mm bore sprockets must be drilled and tapped to accept a 4mm set screw. Use a 3.3mm (#29) drill to drill 2 holes in each sprocket.

(holes should be 90° from each other)

Use 4mm tap to thread (2) holes in each sprocket (total 4 holes)

Install one sprocket on the J3 motor shaft.

Install one sprocket on the J3 spindle shaft.

Cut length of 04B roller chain down to 20-3/4”long. It should have 43 links.

Install connecting link in length of chain and install around both sprockets. Apply grease to chain.

Set tension on chain as tight as possible and tighten motor mount screws. Apply small dab of super glue between mount and arm to lock in place. If mount needs removed glue can be broken with razor knife.

Connect a black, red, and white 22awg with .187” quick disconnect wire to limit switch as shown.

Mount limit switch to J2 arm using (2) M3 X 14 socket head cap screws.

The 4 wires from the J3 motor are not long enough, you will need to extend them. Use solder and heat shrink tube and connect each wire to a length of 22awg wire of matching color.

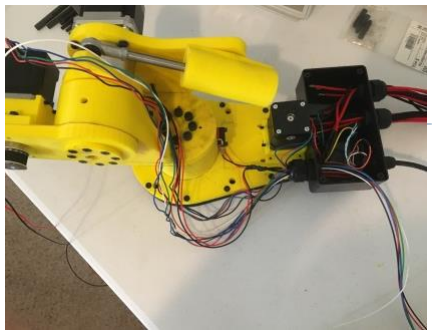
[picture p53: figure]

Pull the (4) extended J3 motor wires as well as the white wire from the J3 limit switch into the enclosure as shown. Make sure to leave appropriate slack shown - this wire loom must have enough slack for J1 & J2 to fully articulate in both directions.

The next step is to connect the (4) J3 motor wires to the correct wires on the ATX cable. You will need to trace the wires from the back of the connector and find the end inside the enclosure.
(Also refer to the ATX pinout diagram and the stepper motor wiring schematic at the end of this manual)

Solder and heat shrink the following connections:
- ATX pin 5 to J3 black
- ATX pin 6 to J3 red
- ATX pin 17 to J3 green
- ATX pin 18 to J3 blue

Use solder and heat shrink tube to connect the white wire from the J3 limit switch to the white/green strip wire from the RJ45 cable.
(Also refer to the wiring schematic at the end of this manual)

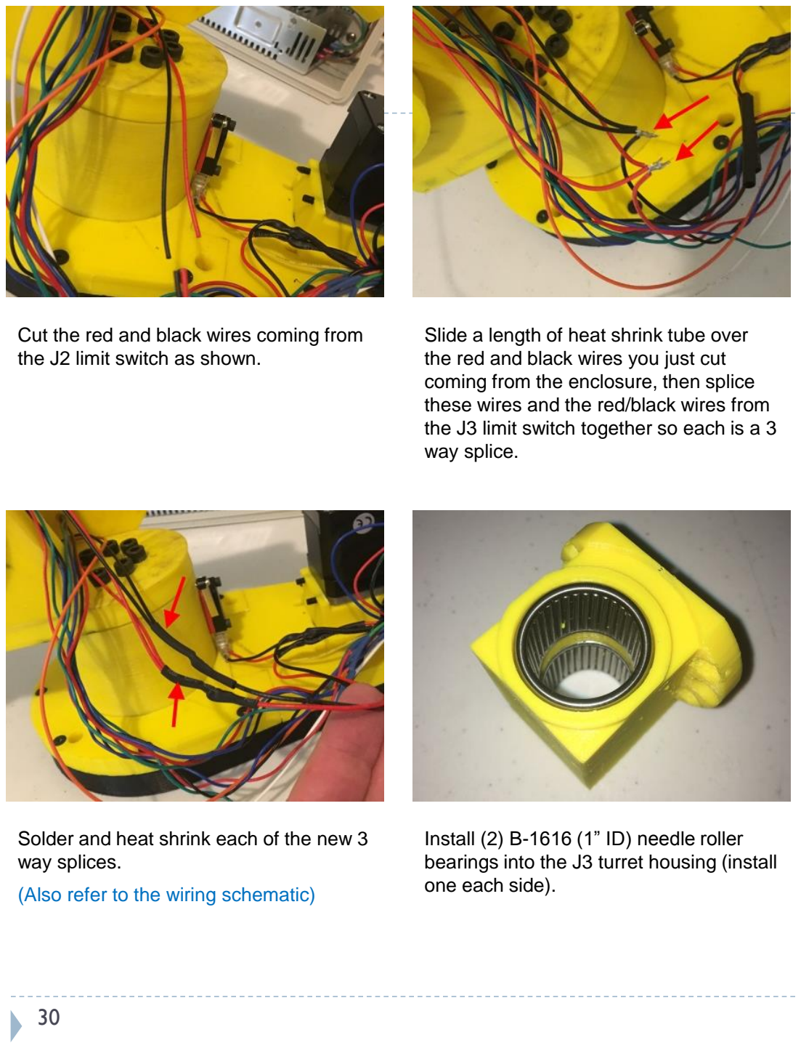
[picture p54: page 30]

Cut the red and black wires coming from the J2 limit switch as shown.

Slide a length of heat shrink tube over the red and black wires you just cut coming from the enclosure, then splice these wires and the red/black wires from the J3 limit switch together so each is a 3 way splice.

Solder and heat shrink each of the new 3 way splices.

(Also refer to the wiring schematic)

Install (2) B-1616 (1” ID) needle roller bearings into the J3 turret housing (install one each side).

Secure turret housing to J3 spindle using
(2) M4 x 14 flat head screws (center)

And (4) M4 x 10 cap screws (outer).

Cut length of high strength aluminum tubing down to 116mm long.

Place tubing next square tube or angle surface to draw line down center.

Drill 3.3 mm hole 18mm from one end and 7mm from other end. Tap both holes to M4.

Insert aluminum tube into J5 motor mount.

Use flashlight to verify alignment of M4 hole in tubing with M4 hole in motor mount.

Install (1) M4 x 5 set screw into J5 motor housing – set screw should just start to thread into tubing. Make sure the M3 timing lug is opposite M4 set screw.

Secure J5 linear screw motor #17LS19-1684E-200G to J5 motor mount using (4) M3 x 14 socket head cap screws. Install (1) M3 x 6 socket head cap screw into motor housing. Note: this screw serves as a timing lug – it is located opposite the holes in the aluminum tube and is referenced in the previous step.

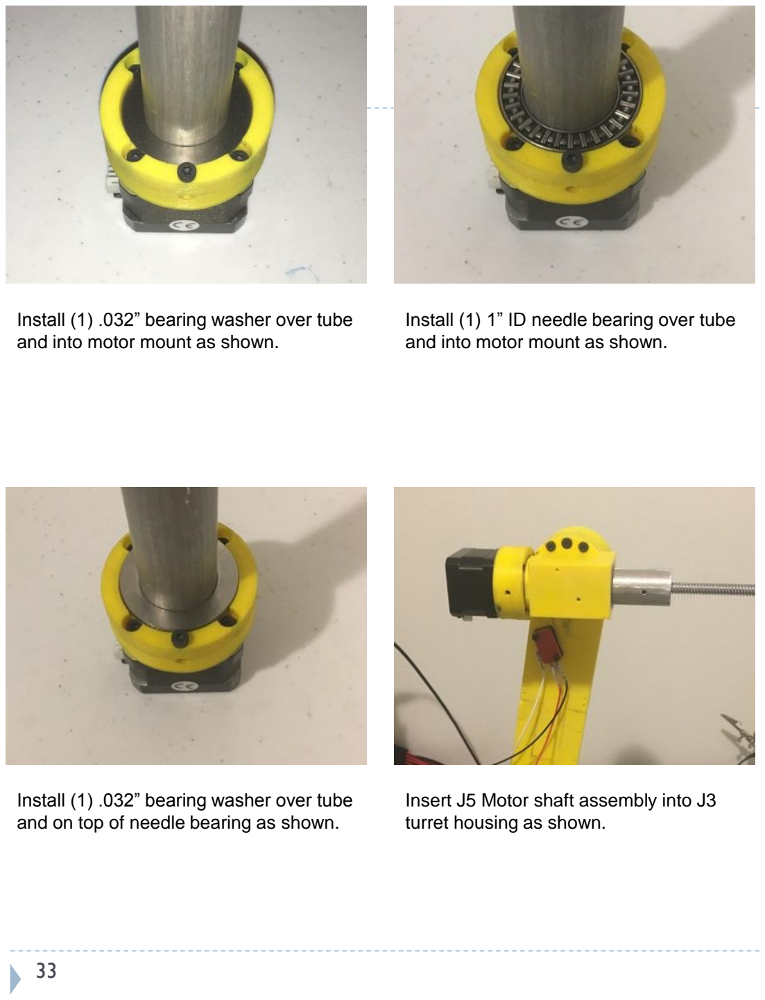
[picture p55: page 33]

Install (1) .032” bearing washer over tube and into motor mount as shown.

Install (1) 1” ID needle bearing over tube and into motor mount as shown.

Install (1) .032” bearing washer over tube and on top of needle bearing as shown.

Insert J5 Motor shaft assembly into J3 turret housing as shown.

Install (1) .032” bearing washer over tube as shown.

Install (1) 1” ID needle bearing over tube and onto .032” bearing washer t as shown.

Install (1) .126” thick bearing washer over thrust bearing as shown.

Install J4 driven pulley with recessed side over thrust bearing/washers. Make sure it is seated firmly and then use 3mm drill to mark tubing. Remove pulley then drill and tap marked position on tube for M4. Do this on both sides of pulley then reinstall pulley.

Install (2) M4 x 6 set screws (opposite sides where holes where drilled/tapped – make sure set screws partially start to thread into tube locking the pulley in place.

Install (4) M3 x 10 set screws into face of pulley and then snug until there is no play in J4 thrust bearings.

Install J4 motor mount / limit switch contact block as shown and secure with
(3) M4 x 10 socket head cap screws.

Install Nema 11 motor mount bracket and secure with (4) M3 x 14 socket head cap screws.

Install 11HS20-0674S-PG5

Geared stepper motor into bracket and secure with (4) M3 x 8 socket head cap screws.

Slide XL 10 tooth 6mm bore drive pulley onto motor shaft along with 84XL037 Gates timing belt simultaneously over J4 driven sprocket. Tighten drive pulley set screw.

Connect a black, red, and blue 22awg with .187” quick disconnect wire to limit switch as shown.

Secure limit switch to J3 turret housing using
(2) M3 x 14 socket head cap screws.
(note the lower screw will need to be ground slightly shorter as this is a very shallow hole – be careful not to strip out hole when assembling ABS robot, use small amount of epoxy on end of screw and allow to cure in place if you have issues)

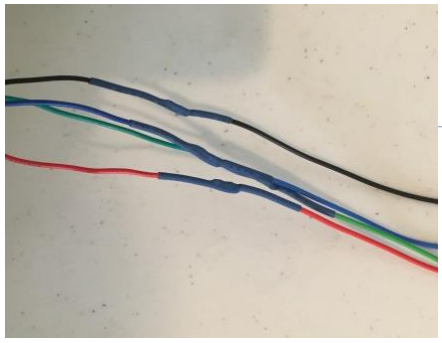
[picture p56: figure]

The 4 wires from the J4 motor are not long enough, you will need to extend them. Use solder and heat shrink tube and connect each wire to a length of 22awg wire of matching color.

Pull the (4) extended J4 motor wires as well as the blue wire from the J4 limit switch into the enclosure as shown. Make sure to leave appropriate slack - this wire loom must have enough slack for J1, J2 and J3 to fully articulate in all directions.

The next step is to connect the (4) J4 motor wires to the correct wires on the ATX cable. You will need to trace the wires from the back of the connector and find the end inside the enclosure.

(Also refer to the ATX pinout diagram and the stepper motor wiring schematic)

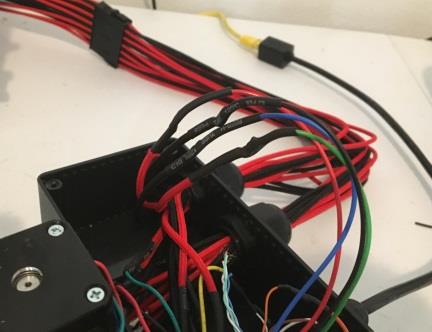
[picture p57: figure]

Solder and heat shrink the following connections:
- ATX pin 7 to J4 black
- ATX pin 8 to J4 red
- ATX pin 19 to J4 green
- ATX pin 20 to J4 blue

Use solder and heat shrink tube to connect theblue wire from the J4 limit switch to the blue/white strip wire from the RJ45 cable.

(Also refer to the wiring schematic)

Cut the red and black wires coming from the J3 limit switch as shown.

Slide a length of heat shrink tube over the red and black wires you just cut coming from the enclosure, then splice these wires with the red/black wires from the J4 limit switch together so each is a 3 way splice.

Solder and heat shrink each of the new 3 way splices.

(Also refer to the wiring schematic)

Install POM nut (supplied with 17LS13-0404E-200H linear motor) into the J5 carrier. Countersink the 3 holes in POM nut and then secure with (3) M3 x 10 flat head screws.

Install (2) LM3UU 3mm linear bearings into J5 carrier then secure with (1) M3 x 6 set screw in bottom hole and (1) M3 x 3 set screw in top hole.

Use abrasive saw to cut (2) 3mm linear rods down to 85mm length.

Install (2) 3mm liner rods into J5 housing and through the J5 carrier bearings as shown. Secure both rods with (2) M3 x 6 set screws – one from the top and one from the bottom . Note: make sure the lower linear rod is not inserted too far, it should not extend into the passage for the screw hole indicated with blur arrow.

Install 688Z 8x16x5mm bearing in end of J5 housing and secure with (2) M3 x 6 set screws from front (shown) and back.

Note: this bearing is press fit – on ABS version also use loctite or adhesive around perimeter of bearing.

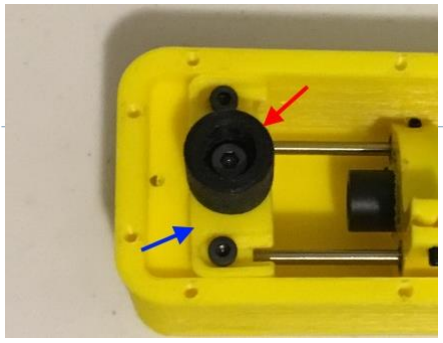
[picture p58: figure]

Install J5 idler tension block (blue arrow) and secure with (2) M3 x 8 socket head cap screws. Then install J5 idler post (red arrow) into tension block and secure with (1) M4 x 10 socket head cap screw.

Install J5 housing onto J4 aluminum tubing (thread motor shaft into POM nut as you go). Make sure the hole indicated with red arrow aligns perfectly with hole in aluminum tube. Note: this hole in housing is too shallow for a set screw and is used for visual alignment only.

On opposite side use 2.5mm drill through center hold shown to mark tubing. Remove housing, finish drilling hole and tap to M3 then reinstall carrier.


Install (1) M3 x 6 set screw into the hole you just tapped.

Make sure set screw just starts to thread into aluminum tube.
Then install 2 more M3 x 6 set screws on top and bottom of carrier to secure housing to tube.

Install #30203 taper roller bearing race into J5 main bearing support arm.

Install #30203 taper bearing onto J6 housing side post.

Install 14HS13-0804S-PG19 geared stepper motor into J6 housing and secure with (4) M3 x 3 set screws. Note: wire harness is 90° to bearing post as shown.

Install (1) .126” thick bearing washer into J6 bearing cap.

Install (1) 1” ID needle bearing into J6 bearing cap.

Install (1) .032” bearing washer into J6 bearing cap on top of bearings.

Use epoxy to secure J6 drive post to J6 housing as shown. (given ABS material the 6 shallow holes do not offer enough support to use screws – holes are used for visual alignment only)

Install J6 motor bearing assembly into bearing support arm with J6 cap assembly on opposite side and secure with (1) M6 x 14 socket head cap screw. Next install (6) M3 x 5 set screws in perimeter of bearing cap and set tension against needle bearings so there is no play in J6 motor assembly.

Connect a black, red, and grey 22awg with .187” quick disconnect wire to limit switch as shown.

Manually rotate the screw shaft on the J5 motor until the J5 belt carrier is all the way to the end of its stroke as shown.

Install J5 limit switch into slot on J6 bearing support arm as shown. Roller on switch should be contacting the J5 belt carrier on inside of housing.


Adjust the switch position until you can hear/feel the switch make contact when you rotate or drive the J5 screw to the top of its stroke. The switch should click right when the belt carrier is reaching the top of its stroke. Secure the switch in place using (2) M4 x 10 set screw on top side of J6 bearing support arm.

Install (1) XL15 tooth – 8mm bore drive sprocket on J6 spindle shaft as shown but do not tighten set screws yet.

Position the J5 side cover as shown.


Install HK1612 bearing over the J5 idler post as shown.

Install 150XL037 gates belt over J5 pulley and idler bearing as shown with belt inserted into the J5 belt carrier.

Set belt tension so belt is tight and there is no play then tighten the M4 screws on the J5 idler tension block.

When using ABS components the M4 screws do not have the holding force to keep tension on the belt under load. Place a small drop of super glue around the heads of the M4 screws securing the head of the screw to the tension block. (if disassembled or tension needs to be reset bond will need to be broken and a new tension block installed)

Rotate J5 shaft until belt carrier is to the top of its stroke and you can feel the J5 limit switch click or make contact.

Use angle gauge and rotate J6 housing until its at 105°


Once angle is at 115° tighten both set screws on sprocket to lock J6 carrier at the correct angle.

Position the J5 spacers as shown.

Install J5 side cover cap as shown. Secure to J5 housing with (8) M3 x 25 flat head screws.

(these go through the cap, spacer and side plate and then thread into the J5 housing)

Secure the the cover & spacer to the side plate on the front using (6) M3 x 20 flat head screws.

(these thread into shallow threads on the side plate)

Extend the 4 wires from the J5 motor connector. They are also not the same colors as the other motors. Use solder and heat shrink tube and connect each wire to a length of 22awg wire. From the plug:

- Red to black extension wire
- Grey to green extension wire
- Yellow to red extension wire
- Green to blue extension wire

Plug the connector into the J5 motor. Leaving plenty of slack for full robot articulation run the 4 wires from J5 and the grey wire from the J5 limit switch into the enclosure.


The next step is to connect the (4) J5 motor wires to the correct wires on the ATX cable. You will need to trace the wires from the back of the connector and find the end inside the enclosure.

(Also refer to the ATX pinout diagram and the stepper motor wiring schematic)

Solder and heat shrink the following connections:
- ATX pin 9 to J5 black
- ATX pin 10 to J5 red
- ATX pin 21 to J5 green
- ATX pin 22 to J5 blue

Use solder and heat shrink tube to connect the grey wire from the J5 limit switch to the white/blue strip wire from the RJ45 cable.

(Also refer to the wiring schematic at the end of this manual)

As done in previous steps splice the red and black wires from the J5 limit switch to the wires going to the J4 limit switch creating a 3 way splice for each.

Solder and heat shrink each of the new 3 way splices.

(Also refer to the wiring schematic at the end of this manual)

Secure J6 gripper mount to SMC MFH2-8D1 gripper using (2) M4 x 10 socket head cap screws.

Insert gripper mount over J6 motor shaft and secure with (2) M4 x 10 set screws.

Insert (1) M4 x 10 socket head cap screw into shoulder of gripper mount. (this will be the contact for the J6 limit switch)

Cut the arm on (1) long straight arm limit switch down to 30mm long as shown.

Cut the remaining piece of the arm down to 14mm long.


Use 6\36\2 rosin core silver bearing electrical solder and soldering iron to melt a blob of solder to end of 14mm piece of arm.

NOTE: THERE IS NOW A 3D PRINTED ARM YOU CAN EPOXY ONTO THE SWITCH- PLEASE SEE UPDATED IN WIRING HARNESS MANUAL

Use soldering stand holder (alligator clips) to hold switch and 14mm extension at 90° -place the blob at joint and use soldering iron to melt blob and secure both pieces together.
NOTE: THERE IS NOW A 3D PRINTED ARM YOU CAN EPOXY ONTO THE SWITCH- PLEASE SEE UPDATED IN WIRING HARNESS MANUAL

Connect a black, red, and green 22awg with .187” quick disconnect wire to limit switch as shown.

Secure limit switch to J6 housing as shown using (2) M3 x 14 socket head cap screws.

As done in previous steps splice the red and black wires from the J6 limit switch to the wires going to the J5 limit switch creating a 3 way splice for each. Use heat shrink tubing and make sure to leave enough slack in the J6 limit switch wire for full articulation of J4 and J5.

Extend the 4 wires from the J6 motor connector. They are also not the same colors as the other motors. Use solder and heat shrink tube and connect each wire to a length of 22awg wire. From the plug:

- Red to black extension wire
- Green to green extension wire
- Yellow to red extension wire
- Blue to blue extension wire


Leaving plenty of slack for full robot articulation run the 4 wires from J6 and the green wire from the J6 limit switch into the enclosure.

The next step is to connect the (4) J4 motor wires to the correct wires on the ATX cable. You will need to trace the wires from the back of the connector and find the end inside the enclosure.

(Also refer to the ATX pinout diagram and the stepper motor wiring schematic)

Solder and heat shrink the following connections:
- ATX pin 11 to J6 black
- ATX pin 12 to J6 red
- ATX pin 23 to J6 green
- ATX pin 24 to J6 blue

Use solder and heat shrink tube to connect the green wire from the J6 limit switch to the green/white strip wire from the RJ45 cable.

(Also refer to the wiring schematic at the end of this manual)

Install (2) J2 side cover spacers and (1) J2 side cover cap as shown.

Apply epoxy to the tops of the 2 side cover spacers.

Install the other 2 side cover spacers and remaining cover cap. In total (28) M3 x 35 flat head screws are used to secure the cover caps and spacers.


Use epoxy to secure auxiliary J2 arm support as shown. Auxiliary support should be epoxied to J2 arm and cover spacers.

The final step in the mechanical assembly procedure is to bundle all the motor and switch wires and encase them in convoluted tubing. (note there are 2 P clips securing the tubing). It is recommended you go through the startup procedure first so that you can fully articulate each joint of the robot and make absolutely sure there is plenty of slack for each axis. This is extremely important and if you don’t make sure the wires have enough slack and stay clear of the switches you will have a great deal of problems with movement and calibration.

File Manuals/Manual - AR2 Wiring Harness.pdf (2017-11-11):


# Model AR2 Wiring Harness

# WIRING HARNESS ASSEMBLY

# BILL OF MATERIALS

## www.omc-stepperonline.com (https://www.omc-stepperonline.com/?tracking=59c1139e8987b)


2

## All Stepper motors, drivers and power supplies are available at:


3


4


5

(Make sure you buy high quality non roller switch for J6 – note the rivet hinge pin)


6

## You will need 1 limit switch tip

For J6, this part must be 3D printed.

## The print file can be found on The project page with all the other

3D print files.

# SECTION 1

# FEMALE 4 PIN JST CONNECTOR FOR MOTOR END OF WIRING HARNESS

7

NOTE THAT THE GAP ON THE PIN INSULATION WINGS IS TYPICALLY TOO WIDE OR TOO OPEN.

BEND AND BREAK OFF FEMALE PIN FROM STRIP.

THE GAP SHOULD NOW LOOK LIKE THIS.

USE NEEDLE NOSE PLIERS TO CLOSE THE GAP AS SHOWN

STRIP END LEAVING APPROX 3mm OF WIRE EXPOSED ON ALL 4 WIRES.

PLACE END OF RIBBON WIRE IN SELF ADJUSTING WIRE STRIPPERS AS SHOWN.

NOTE THE LIP OR STEP IN THE UPPER JAW OF THE CRIMPING TOOL.

USE CUTTERS OR RAZOR KNIFE TO SEPARATE WIRES.

CLOSE THE CRIMPER SLOWLY INTIL THE RATCHET MECHANISM CLICKS 3 TIMES BUT DO NOT FULLY CLAMP. IT SHOULD LOOK LIKE THIS.

WITH CRIMPING TOOL UPSIDE DOWN IN YOUR LEFT HAND PLACE THE FEMALE PIN INTO THE JAW WITH YOUR RIGHT HAND AS SHOWN. THE WINGS
SHOULD BE UP AGAINST THE STEP SHOWN IN THE PREVIOUS STEP..

THIS PICTURE SHOWS WHERE THE WIRE SHOULD BE SITTING INSIDE THE PIN.

NOTE THE JACKET IS JUST PAST THE LARGE WINGS AND THE WIRE ITESELF IS INSIDE THE SMALLER SET OF WINGS.

IT WILL TAKE PRACTICE TO GET A FEEL FOR HOW TO INSERT THE WIRE INTO THE CRIMPER TO GET THIS ALIGNMENT.

FLIP THE CRIMPER BACK RIGHT SIDE UP AND HOLD WITH YOUR RIGHT HAND, THEN STARTING WITH THE BLUE WIRE AS SHOWN – INSERT THE WIRE INTO THE CRIMPER AND PIN.

THIS PICTURE SHOWS HOW IT SHOULD LOOK AFTER BEING CRIMPED.

NOTE THE JACKET IS FULLY CLAMPED BY THE LARGE WINGS BUT THE JACKET STOPS RIGHT AT THE SMALLER WINGS AND THE SMALLER WINGS HAVE CLAMPED ONLY THE METAL WIRE.

I SUGGEST PRACTICING THIS SEVERAL TIMES TO GET THE HANG OF IT BEFORE TRYING TO MAKE YOUR WIRING HARNESS.

WITH THE WIRE AT THE CORRECT DEPTH COMPETEY CLAMP THE CRIMPER.

THIS PICTURE ALSO SHOWS AN INCORRECTLY CRIMPED
CONNECTOR.

NOTE THE WIRE WAS INSERTED TOO FAR AND THE JACKET IS
CLAMPED BY BOTH THE LARGE
AND SMALL WINGS.

THIS IS NOT ACCEPTABLE – IF IT LOOKS LIKE THIS YOU NEED TO RE-DO IT..

THIS PICTURE SHOWS AN
INCORRECTLY CRIMPED
CONNECTOR.

NOTE THE JACKET IS NOT FULLY INSIDE OR CLAMPED BY THE
WINGS.

THIS IS NOT ACCEPTABLE – IF IT LOOKS LIKE THIS YOU NEED TO RE-DO IT.

CUT A LENGTH OF HEAT SHRINK TUBING APPROX 25mm LONG AND RUN WIRES THROUGH IT AS SHOWN.

ONCE YOU HAVE MASTERED CRIMPING CONTINUE CRIMPING A PIN ON ALL 4 WIRES AS SHOWN.

PINCH EACH CONNECTOR IN YOUR FINGERS AND TUG ON IT TO MAKE SURE IT DOESN’T COME OFF EASILY. IF IT COMES OFF IT OBVIOSLY NEEDS TO BE REDONE AND WASN’T FULLY CRIMPED.

START TO FEED WIRES INTO FEMALE HOUSING AS SHOWN.

USE A RAZOR BLADE TO MAKE SURE THE TANGS ON EACH PIN ARE POINTED OUT.

SOMETIMES THEY GET FLATTENED AND WILL NOT LATCH INTO THE PLASTIC HOUSING.

APPLY BLACK SILICONE AROUND THE BASE OF THE CONNECTOR ON BOTH SIDES AS SHOWN.

CONTINUE TO FULLY INSERT WIRES INTO HOUSING.

NOTE THE TANGS ARE FULLY INSERTED INTO THE SLOTS AND DO NOT PULL BACK OUT

NOTE WITH THE SLOTS FACING YOU THE BLUE WIRE IS ON TOP, THEN RED, GREEN AND BLACK ON THE BOTTOM. IT IS IMPORTANT THEY ARE INSERTED IN THIS ORDER.

AFTER WORKING SILICONE INTO CONNECTOR SPREAD IT A SHORT WAY DOWN THE WIRES – IT SHOULD LOOK LIKE THE PICTURE.

USE A TOOTHPICK TO WORK SILICONE INTO EACH JACKET ON BOTH SIDES.

USE A HEAT GUN TO SHRINK THE TUBING AS SHOWN.

THIS CONNECTOR IS NOW COMPLETE

SLIDE THE LENGTH OF HEAT SHRINK TUBING OVER THE CONNECTOR AS SHOWN.

# SECTION 2

## FEMALE 3 PIN JST CONNECTOR FOR LIMIT SWITCH END OF WIRING HARNESS

21

INSERT WIRES WITH FEMALE PINS INTO THE 3 PIN FEMALE JST HOUSING AS SHOWN.

NOTE WITH THE SLOTS FACING YOU THE RED WIRE IS ON TOP, THEN GREEN AND BLACK ON THE BOTTOM. IT IS IMPORTANT THEY ARE INSERTED IN THIS ORDER.

REMOVE THE BLUE STRAND FROM THE RIBBON WIRE AS THIS CONNECTOR ONLY REQUIRES 3 WIRES.

CRIMP FEMALE PINS TO THE ENDS OF EACH OF THE WIRES STARTING WITH THE RED WIRE AS SHOWN – REFER TO INSTRUCTIONS IN SECTION 1 FOR CRIMPING DETAILS.

APPLY SILICONE AND HEAT SHRINK TUBING AS OUTLINED IN SECTION 1.

THIS CONNECTOR IS NOW COMPLETE.

# SECTION 3

# MALE 3 PIN JST CONNECTOR LIMIT SWITCH PIGTAILS

24

NOTE THE LIMIT SWITCH FOR AXIS 6 USES A STRAIGH ARM LIMIT SWITCH WITH THE J6 LIMIT SWITCH TIP ATTACHED.

LIGHTLY SAND END OF LIMIT SWICH ARM ON BOTH SIDES AND THEN USE EPOXY TO SECURE J6 LIMIT SWITCH TIP TO ARM OF SWITCH.

.STL PRINT FILE FOR THIS TIP CAN BE FOUND ON PROJECT PAGE INCLUDED WITH THE OTHER PRINT FILES FOR THE COMPLETE PRINTED ROBOT.

CONNECT BLACK, RED AND GREY 22 AWG QUICK DISCONNECT WIRES TO EACH LIMIT SWITCHES FOR ALL 6 AXIS.

NOTE: J1 THROUGH J5 WILL USE THE ROLLER LIMIT SWICH SHOWN. J6 WILL USE A STRAIGH ARM WITH TIP EXTENSION SHOWN IN THE NEXT STEP.

## Cut quick disconnect wires to length for each switch as shown below


26

INSERT WIRES INTO MALE JST HOUSING AS SHOWN –WITH CLIP FACING FORWARD INSERT RED WIRE ON TOP, GREY IN THE MIDDLE AND BLACK ON THE BOTTOM.

CRIMP JST MALE PINS TO RED, GREY AND BLACK WIRES IN THE EXACT SAME PROCEEDURE OUTLINED IN SECTION 1 FOR ALL 6 LIMIT SWITCHES.

PLACE SILICONE AROUND WIRES AT BASE OF JST HOUSING AND WORK SILICONE INTO REAR OF CONNECTOR IN THE SAME WAY SHOWN IN SECTION 1.

INSERT PINS UNTIL THEY ARE FULLY SEATED AND CLICK INTO THE
HOUSING.

PLACE SHORT LENGTH OF HEAT SHRINK TUBE OVER WIRES AND ONTO JST CONNECTOR AS SHOWN.

WRAP WIRES WITH 4mm SPIRAL WRAP – MAKE SURE SPIRAL WRAP EMBEDS INTO SILICONE BEFORE IT CURES.

AFTER ALL 6 LIMIT SWITCH PIGTAILS ARE COMPLETE USE PAINT PENS TO MARK THE CONNECTORS AS SHOWN ON THE NEXT PAGE

USE HEAT GUN TO SHRINK TUBING AROUND CONNECTOR AND WIRES.

## MARK CONNECTORS AS SHOWN


31

# SECTION 4

# MALE 4 PIN JST CONNECTOR ON MOTOR PIGTAILS

32

## CUT MOTOR WIRES TO THE FOLLOWING LENGTHS


33

SLIDE SHORT LENGTH OF HEAT SHRINK TUBE OVER WIRES.

CRIP MALE JST PINS AS OUTLINED IN SECTION 1TO EACH WIRE ON ALL 6 MOTORS.

INSERT WIRES INTO MALE JST HOUSING AS SHOWN. – MAKE SURE THEY FULLY CLICK INTO PLACE.

MAKE SURE WITH THE CLIP FACING YOU THAT THE BLUE WIRE IS ON THE LEFT, THEN THE RED, GREEN, AND BLACK ON THE RIGHT.

WRAP 4mm SPIRAL WRAP AROUND WIRES AND SLIDE UNDER HEAT SHRINK WRAP AS ITS WRAPPED.

FINSIH WRAPPING SPRIRAL WRAP INTIL WRAP IS EMBEDDED INTO SILICONE..

APPLY BLACK SILICONE TO WIRES AND CONNECTOR –WORK SILICONE INTO BACK OF CONNECTOR WITH TOOTH PICK.

USE HEAT GUN TO SHRINK TUBING AS SHOWN.

SLIDE HEAT SHRINK TUBE OVER CONNECTOR AS SHOWN.

APPLY BLACK SILICONE TO THE BASE OF EACH PIGTAIL.


## MARK EACH CONNECTOR WITH PAINT PENS AS SHOWN


39

# SECTION 5

# WIRING HARNESS ASSEMBLY

40

## CUT 6 LENTHS OF 4-STRAND RIBBON WIRE TO THE


41

## FOLLOWING LENTHS:

### J1-WIRE = 28cm (11”) LONG

### J2-WIRE = 58.5cm (23”) LONG

### J3-WIRE = 58.5cm (23”) LONG

### J4-WIRE =73.5cm (29”) LONG

### J5-WIRE = 73.5cm (29”) LONG

### J6-WIRE = 119.5cm (47”) LONG

IN THE NEXT STEP WE NEED TO CONNECT MALE ATX PINS TO EACH WIRE ON OPPOSITE END OF WIRE.

THIS IS DONE IN THE SAME MANNOR OUTLINED IN SECTION 1 –THE ONLY DIFFERENCE IS YOU WILL USE THE 2ND SLOT ON THE CRIMPER AS SHOWN IN THE PHOTO ON THE RIGHT (THE ATX PINS ARE ONE SIZE LARGER THAN THE JST PINS)

YOU WILL ALSO NEED TO CLOSE THE CRIMPER 2 CLICKS TO SECURE THE PIN JUST PRIOR TO CRIMPING.


CONNECT 4 PIN FEMALE JST
CONNECTOR TO ONE END OF EACH WIRE AS OUTLINED IN SECTION 1.

USE A MULTIMETER ON CONTINUITY SETTING TO CHECK FOR A GOOD CONNECTION FROM THE MALE ATX PIN ON ONE END TO THE
COORESPONDING JST FEMALE PIN AT THE OTHER END.

USE AN UNUSED JST PIN TO PROBE THE FEMALE CONNECTOR AS SHOWN.

CHECK CONTINUITY FOR EVERY STRAND ON ALL 6 WIRES.

CONNECT MALE ATX PIN TO EACH WIRE.

THE FOLLOWING 6 STEPS WILL OUTLINE COLOR CODING EACH WIRE WITH A PAINT PEN.

FOR THE J1 WIRE (11” long) DO NOT APPLY ANY PAINT.

AS A PRECAUTION COAT THE
CONNECTION FROM THE ATX PIN WINGS TO THE WIRE INSULATION IN SUPER GLUE AS ADDITIONAL
PROTECTION FROM WIRES PULLING OUT WHILE UNDER STRESS.

FOR THE J3 WIRE (23” long) APPLY RED PAINT TO BOTH ENDS OF THE WIRE.

FOR THE J2 WIRE (23” long) APPLY BLUE PAINT TO BOTH ENDS OF THE WIRE.

FOR THE J5 WIRE (29” long) APPLY WHITE PAINT TO BOTH ENDS OF THE WIRE.

FOR THE J4 WIRE (29” long) APPLY YELLOW PAINT TO BOTH ENDS OF THE WIRE.


IN THE FOLLOWING STEPSWE WILL INSERT THE ATX PINS INTO THE ATX HOUSING.

THE IMAGE TO THE RIGHT SHOWS HOW THE WIRES SHOULD BE INSERTED FROM THE PERSPECTIVE OF LOOKING AT THE BACKSIDE OF THE CONNECTOR WHERE THE WIRES ARE COMING OUT..

FOR THE J6 WIRE (47” long) DO NOT APPLY ANY PAINT.

APPLY BLACK SILICONE TO REAR OF CONNECTOR ON BOTH SIDES AND WORK SILICONE INTO CONNECTOR WITH A TOOTHPICK.

INSERT THE WIRES INTO THE ATX CONNECTOR AS SHOWN AND PER THE PREVIOUS DIAGRAM.

## CUT 6 LENTHS OF STRANDED RIBBON WIRE TO


49

## THE FOLLOWING LENTHS – STRIP OFF THE BLUE WIRE FROM EACH SO THAT YOU

HAVE 3 STRAND WIRES (RED,

### GREEN, BLACK):

### J1-WIRE = 28cm (11”) LONG

### J2-WIRE = 58.5cm (23”) LONG

### J3-WIRE = 73.5cm (29”) LONG

### J4-WIRE =73.5cm (29”) LONG

### J5-WIRE = 119.5cm (47”) LONG

### J6-WIRE = 119.5cm (47”) LONG

### THES 6 WIRES WILL BE FOR THE

LIMIT SWITCHES.

STRIP 6mmTO 8mm FROM THE OTHER END OF THE LIMIT SWITCH WIRES

INSTALL 3 PIN FEMALE JST CONNECTOR AS OUTLINED IN SECTION 2 ON THE END OF EACH OF THE 6 LIMIT SWITCH WIRES.

USE RED PAINT PEN TO MARK THE J3 LIMIT SWITCH WIRE (29” long) AT BOTH ENDS AS SHOWN.

USE BLUE PAINT PEN TO MARK THE J2 LIMIT SWITCH WIRE (23” long) AT BOTH ENDS AS SHOWN.

NOTE: AS BEFORE THE J1 WIRE DOES NOT NEED TO BE MARKED.

USE WHITE PAINT PEN TO MARK THE J5 LIMIT SWITCH WIRE (47” long) AT BOTH ENDS AS SHOWN.

NOTE: AS BEFORE THE J6 WIRE DOES NOT NEED TO BE MARKED.

USE YELLOW PAINT PEN TO MARK THE J4 LIMIT SWITCH WIRE (29” long) AT BOTH ENDS AS SHOWN.

CUT OFF MALE END OF RJ45
EXTENSION WIRE AND STRIP OFF OUTER SHEETHING AS SHOWN.

ON THE STRIPPED END OF LIMIT SWITCH WIRES – SEPARATE THE WIRE STRANDS THEN TWIST ALL THE RED WIRES TOGETHER AND THEN TWIST ALL THE BLACK WIRES TOGETHER.

SLIP 2.5cm (1”) LENGTH OF 6mm HEAT SHRINK TUBING OVER RED AND BLACK WIRE BUNDLES.

SLIP 2.5cm (1”) LENGTH OF 2mm HEAT SHRINK TUBING OVER EACH OF THE GREEN WIRES.

SLIP 10cm (4”) LENGTH OF 10mm HEAT SHRINK TUBING OVER RJ45 WIRES. THEN STRIP ENDS OF EACH WIRE.

SOLDER BROWN WIRE FROM RJ45 TO THE GROUP OF RED WIRES AS SHOWN.


THE FOLLOWING STEPS WILL
CONNECT THE GREEN LIMIT SWITCH WIRES TO THE CORRECT RJ45 WIRES. THE IMAGE TO THE LEFT SHOWS THE COLOR CODE FOR WHICH RJ45 WIRE GOES TO WHICH LIMIT SWITCH

J1 = WHITE / ORANGE STRIPE
J2 = ORANGE / WHITE STRIPE J3 = WHITE / GREEN STRIPE
J4 = BLUE / WHITE STRIPE
J5 = WHITE / BLUE STRIPE
J6 = GREEN / WHITE STRIPE
COMMON NEGATIVE = WHITE / BROWN STRIPE.
COMMON POSITIVE = BROWN / WHITE STRIPE.

SOLDER WHITE / BROWN STRIPE WIRE TO THE GROUP OF BLACK WIRES.

SLIDE HEAT SHRINK TUBE OVER SOLDER JOINT AND USE HEAT GUN TO SHRINK TUBE.

TRACE UNPAINTED GREEN WIRE FROM SHORT J1 LIMIT SWITCH WIRE AND SOLDER TO THE WHITE / ORANGE STRIPE WIRE.

THEN SLIDE HEAT SHRINK TUBE OVER SOLDER JOINT AND SHRINK WITH HEAT GUN.

SLIDE HEAT SHRINK TUBE OVER SOLDER JOINT AND USE HEAT GUN TO SHRINK TUBE.

FIND THE J3 LIMIT SWITCH WIRE
WHICH WAS MARKED WITH RED PAINT PEN AND SOLDER TO THE WHITE / GREEN STRIPE WIRE.

THEN SLIDE HEAT SHRINK TUBE OVER SOLDER JOINT AND SHRINK WITH HEAT GUN.

FIND THE J2 LIMIT SWITCH WIRE WHICH WAS MARKED WITH BLUE PAINT PEN AND SOLDER TO THE ORANGE / WHITE STRIPE WIRE.

THEN SLIDE HEAT SHRINK TUBE OVER SOLDER JOINT AND SHRINK WITH HEAT GUN.

FIND THE J5 LIMIT SWITCH WIRE WHICH WAS MARKED WITH WHITE PAINT PEN AND SOLDER TO THE WHITE / BLUE STRIPE WIRE.

THEN SLIDE HEAT SHRINK TUBE OVER SOLDER JOINT AND SHRINK WITH HEAT GUN.

FIND THE J4 LIMIT SWITCH WIRE WHICH WAS MARKED WITH YELLOW PAINT PEN AND SOLDER TO THE BLUE / WHITE STRIPE WIRE.

THEN SLIDE HEAT SHRINK TUBE OVER SOLDER JOINT AND SHRINK WITH HEAT GUN.

SLIDE THE LARGE 10mm HEAT SHRINK TUBE OVER THE ENTIRE BUNDLE OF JOINTS AND USE HEAT SHRINK GUN TO SHRINK TUBING.

FIND THE REMAINING J6 LIMIT SWITCH WIRE WHICH WAS NOT MARKED AND SOLDER TO THE GREEN / WHITE STRIPE WIRE.

THEN SLIDE HEAT SHRINK TUBE OVER SOLDER JOINT AND SHRINK WITH HEAT GUN.


LAY THE LIMIT SWITCH WIRE BUNDLE OVER THE MOTOR WIRES BUNDLE WITH SOLDER JOINT OVER THE TOP OF THE ATX CONNECTOR AND THE J1 MOTOR CONNECTOR ALIGNED WITH THE J1 LIMIT SWITCH CONNECTOR AS SHOWN.

IF YOU WILL BE USING A PNEUMATIC GRIPPER LAY PNEUMATIC LINES ALONG WITH WIRE BUNDLES. THE PNEUMATIC LINES CAN BE AS LONG AS YOU WANT BUT MAKE SURE THE PNEUMATIC LINES EXTEND APPROX 8” PAST THE J6 CONNECTORS AT THE VERY END OF THE HARNESS.


WITH MOTOR BUNDE, LIMIT SWITCH BUNDLE AND PNEUMATIC LINES ALL GROUPED TOGETHER TIE THE ENTIRE BUNDLE TOGETHER WITH A SMALL ZIP TIE WHERE SHOWN.

WRAP BUNDLE WITH 10mm SPIRAL WRAP AS SHOWN –WHEN YOU ARE 17.8cm (7”) FROM END OF ATX CONNECTOR PULL THE J1 MOTOR AND LIMIT WIRES OUT OF THE BUNDLE.


CONTINUE WRAPPING SPIRAL WRAP PAST THE SPOT WHERE THE J1 WIRES EXIT THE WRAP – THEN ATTACH A MOUNTING CABLE TIE AS SHOWN 15.5cm (6”) FROM ATX CONNECTOR

CONTINUE WRAPING BUNDLE WITH SPIRAL WRAP –WHEN YOU ARE 40.5cm (16”) FROM ATX CONNECTOR PULL THE J2 MOTOR AND LIMIT WIRES AS WELL AS THE J2 MOTOR OUT OF THE WRAP AS SHOWN.


CONTINUE WRAPPING BUNDLE WITH SPIRAL WRAP –WHEN YOU GET JUST PAST 69cm FROM ATX CONNECTOR BREAK THE J4 AND J5 MOTOR CONNECTORS AND J2 AND J4 LIMIT CONNECTORS OUT OF THE WRAP. THEN PLACE A MOUNTING CABLE TIE 68.5cm FROM ATX CONNECTOR.

CONTINUE WRAPPING BUNDLE AND PLACE ANOTHER MOUNTING CABLE TIE 15.25cm (6”) FROM PREVIOIUS CABLE TIE.


CONTINUE WRAPPING SPIRAL WRAP ALL THE WAY TO THE J6 CONNECTORS AS SHOWN. INSTALL MOUNTING CABLE TIE AT END OF SPIRAL WRAP AS SHOWN.

GO BACK TO THE J2 & 3 MOTOR AND LIMIT WIRES THAT EXIT THE LOOM AND WRAP THEM IN SPIRAL WRAP AND THEN WRAP THE JOINT WITH ELECTRICAL TAPE AS SHOWN.

## WIRING HARNESS IS NOW COMPLETE


66

# SECTION 6

# WIRING HARNESS INSTALLATION

67

SECURE THE HARNESS TO THE J2 ARM USING M4 SCREWS THROUGH THE CABLE TIE MOUNTS AS SHOWN.

SECURE HARNESS TO BASEPLATE USING M4 SCREW ANDTHEN CONNECT THE J1 MOTOR AND LIMIT SWITCH
CONNECTORS.

CONNECT THE J2 & J3 MOTOR
CONNECTORS AND THE J2 LIMIT SWITCH CONNECTOR AS SHOWN.

ROUTE THE J2 & J3 MOTOR AND LIMIT SWITCH WIRES THROUGH THE CENTER OF ROBOT AND THEN SECURE TO THE J2 MOTOR SUPPORT PLATE USING A STANDARD CABLE TIE THROUGH THE SIDE HOLE AS SHOWN.

THE CABLE TIE SHOULD REMAIN LOOSE AROUND THE WIRES – JUST TIGHT ENOUGH SO THE CONNECTORS CANT SLIP THROUGH THE TIE AND THE WIRES CANT SWING INTO THE J2 LIMIT SWITCH.

SECURE THE END OF THE HARNESS TO THE J5 SUPPORT ARM AS SHOWN USING A M4 SCREW AND THEN CONNECT THE J5 & J6 CONNECTORS AS WELL AS THE PNEUMATIC GRIPPER TUBES.

THIS CONCLUDES THE WIRING
HARNESS MANUAL – PLEASE VISIT THE PROJECT PAGE AND REVIEW THE VIDEO ON STARTUP AND
CALIBRATION.

CONNECT THE J4 & J5 MOTOR AND LIMIT SWITCH CONNECTORS AS SHOWN.

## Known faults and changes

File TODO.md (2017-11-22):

# Control Point 3 todo

- Manuals
  - BOM (Wagner Batalha)
  - Assembly instructions (Wagner Batalha)
  - Maintenance
- Pricing of the parts (Igor Lima, Lucas Regis)
- Create a DMU kinematic simulation under CATIA. (Marcos Paulo)
- Structural Simulation on ANSY (Jonatas Riberiro)
- Remake the requirements (Luís Lahr)

Done
- Create The Primary Assembly and CADs. The list of parts that need CAD are on the file: `Parts that need CAD.md`

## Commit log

2017-11-02 First commit. Converted STEP files to CATpart and created a basic Assembly, badly in need of more pieces
    [AR2ASSY.CATProduct, J1 & J3 motor mount - precision GB.CATPart, J1 base plate.CATPart, J1 base support spacer.CATPart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]
2017-11-02 Added some color
    [AR2ASSY.CATProduct, J1 base plate.CATPart, J1 base support spacer.CATPart, J1 motor mount.CATPart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]
2017-11-04 Organized the assembly. Inserted some fasteners
    [30206 taperedRollerBearing.CATPart, 45x75x15_TaperedRollerBearing.CATPart, AR2ASSY.CATProduct, J1 base plate.CATPart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]
2017-11-04 Inserted some fasteners
    [AR2ASSY.CATProduct, J1 base plate.CATPart, J1 base support spacer.CATPart, M4x10 SOCKET HEAD SCREW.CATPart]
2017-11-10 added some parts and created some CADs to the assembçy
    [30204 taperedRollerBearing.CATPart, 30206 taperedRollerBearing.CATPart, 45x75x15_TaperedRollerBearing.CATPart, 5909K360_THRUST NEEDLE-ROLLER BEARING.CATPart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]
2017-11-11 Added some new parts, fixed links on AR2ASSY.CATProduct.
    [3mm liner rod.CATPart, AR2ASSY.CATProduct, J4 bearing.CATPart, J4 driven Pulley.CATPart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]
2017-11-14 Added a pom nut, modified the j5 side cover, and added a drawing
    [AR2ASSY.CATProduct, J2 side cover.CATPart, J5 Tube.CATPart, J5 side cover cap.CATPart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]
2017-11-15 Added 17HS19 Motor to assembly
    [5.1 Planetary Gear 17HS19-1684S-PG5 NEMA 17 Stepper Motor.CATPart, AR2ASSY.CATProduct, M3x5 SOCKET HEAD SCREW.CATPart]
2017-11-17 added 5:1reduction Nema 17 Motor to assembly. Changed Base plate to acomodate Screws
    [5.1 Planetary Gear 17HS19-1684S-PG5 NEMA 17 Stepper Motor.CATPart, AR2ASSY.CATProduct, J1 base plate.CATPart]
2017-11-17 Added Threaded Rod NEMA 17 external link 200mm T8
    [Threaded Rod NEMA 17 external link 200mm T8 x 8_(Assembly).CATPart]
2017-11-17 Create Threaded Rod NEMA 17 external link 200mm T8 x 8 (Product)
2017-11-17 Threaded Rod NEMA 17 external link 200mm T8 x 8 (Product)
2017-11-17 added more motors to Assembly, fixed some dimensions
    [19.1 Planetary Gear 17HS19-1684S-PG19 NEMA 17 Stepper Motor.CATPart, 5.1 Planetary Gear 17HS19-1684S-PG5 NEMA 17 Stepper Motor.CATPart, AR2ASSY.CATProduct, Nem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]
2017-11-17 Deleted unecessary file
    [Threaded Rod NEMA 17 external link 200mm T8 x 8_(Assembly).CATPart]
2017-11-17 Added more motors and screws
    [19.1 Planetary Gear 14HS13-0804S-PG19 NEMA 14 Stepper Motor.CATPart, 19.1 Planetary Gear 17HS19-1684S-PG19 NEMA 17 Stepper Motor.CATPart, AR2ASSY.CATProduct, E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]
2017-11-17 moved motors to their folder
    [19.1 Planetary Gear 17HS19-1684S-PG19 NEMA 17 Stepper Motor.CATPart, 5.1 Planetary Gear 17HS19-1684S-PG5 NEMA 17 Stepper Motor.CATPart, AR2ASSY.CATProduct, Nem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]
2017-11-17 moved Bearings to their folder
    [30203 Tapered Bearing.CATPart, AR2ASSY.CATProduct, SKF HK 1612 Needle Roller Bearing Caged 16mmID 22mmOD 12Width.CATPart, Thrust Needle Roller Bearing 35x52x4.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]
2017-11-19 added more parts to assy. Created some parts
    [30203 Tapered Bearing.CATPart, AR2ASSY.CATProduct, J5 Idler Post.CATPart, J5 side cover cap.CATPart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]
2017-11-23 Moved all parts to their respective joints
    [AR2ASSY.CATProduct, J1 base plate.CATPart, J1 base support spacer.CATPart, J1 motor mount.CATPart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]
2017-11-24 created basic cinematics simulation
    [AR2 Kinematics Simulation.CATProduct, Joint1_AllCATPart.CATPart, Joint2_AllCATPart.CATPart, Joint3_AllCATPart.CATPart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]
2017-11-24 Added Assembly instructions
    [AR2 Kinematics Simulation.CATProduct]
2017-11-30 Added more screws. Created Assembly instructions
    [AR2ASSY.CATProduct, BaseTransdutor.CATPart, Eixo_do_motor.CATPart, J1 base plate.CATPart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]
2017-12-01 Added a manekin to kinematic simulation. Translated Instructions
    [AR2 Kinematics Simulation.CATProduct, J5 side cover cap.CATPart]
